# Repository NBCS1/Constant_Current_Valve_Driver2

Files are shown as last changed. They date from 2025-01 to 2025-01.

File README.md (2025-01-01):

# Constant_Current_Valve_Driver
Harware and firmware associated with controlling 4 bistable valves from TTL pulse of various duration. The Pulse is coming from a Pressure controller and its software were only the duration can be set. Different durations trigger different combinations of valves in the context of a microfluidic system.
The valves are bistable and require a pulse of constant current to turn ON/OFF. 
The code can be modified to have any pulse duration and the hardware can be modified to also obtain stable current from 0 to 1.5A.
The stable current is based on a AL8860 ic.
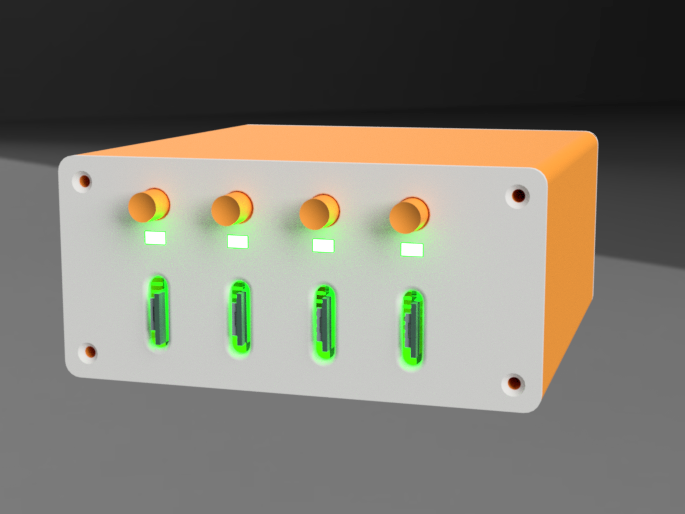
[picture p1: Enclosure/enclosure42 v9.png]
Enclosure


Disclaimer: We will not be responsible in case any implementation of the content of this repository leads to damage in instruments or components.

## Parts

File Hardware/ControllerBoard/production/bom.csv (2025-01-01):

Designator | Footprint | Quantity | Value | LCSC Part #
J1, J2 | PinHeader_1x15_P2.54mm_Vertical | 2 | Conn_01x15_Pin
J10 | PinSocket_1x12_P2.54mm_Vertical | 1 | register_out
J3 | TerminalBlock_Phoenix_PT-1,5-2-5.0-H_1x02_P5.00mm_Horizontal | 1 | power
J4 | PinSocket_1x04_P2.54mm_Vertical | 1 | LEDS_vcc
J5 | PinSocket_1x04_P2.54mm_Vertical | 1 | LEDS_gnd
J6 | PinSocket_1x04_P2.54mm_Vertical | 1 | Buttons_digital
J7 | PinSocket_1x04_P2.54mm_Vertical | 1 | BUTTONS_gnd
J8 | PinSocket_1x04_P2.54mm_Vertical | 1 | oled
J9 | PinSocket_1x02_P2.54mm_Vertical | 1 | TTLin
R1, R2, R3 | 1206 | 3 | 10k
RV1, RV2, RV3, RV4 | Potentiometer_Vishay_T73XW_Horizontal | 4 | potentiometer_3362P
U1, U2 | D16-M | 2 | SN74HC595_N_16
U3 | D14-M | 1 | LM324N
U4 | SOIC20 | 1 | 74HC540D
U5, U6 | SOT108-1_NEX-M | 2 | 74HC08D_652

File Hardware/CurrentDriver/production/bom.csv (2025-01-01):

Designator | Footprint | Quantity | Value | LCSC Part #
C1, C2, C3, C4 | 0805 | 4 | C10µF_0805
C5, C7 | 0805 | 2 | C0.100µF_0805
C6, C8 | 0805 | 2 | C0.0.1µF_0805
D1 | D_SOD-123F | 1 | SS24FL
D2, D4, D6, D7 | 0805 | 4 | LG R971-KN1
J1 | PinHeader_1x04_P2.54mm_Vertical | 1 | Conn_01x04
J10 | PinHeader_1x08_P2.54mm_Vertical | 1 | Conn_01x08
J3 | TerminalBlock_Phoenix_PT-1,5-2-5.0-H_1x02_P5.00mm_Horizontal | 1 | power
J4 | CON_527460871_MOL | 1 | 527460871
L1 | IND_BOURNS_RLB0914 | 1 | RLB0914-37µH
R1 | 1206 | 1 | R125m_1206
R10, R11, R6, R8 | 1206 | 4 | 150ohms
R2, R3 | 1206 | 2 | 7kohms
R4, R5 | 1206 | 2 | 10kohms
U1, U2 | TSOT26-P7_DIO | 2 | AP22615AWU-7
V1 | TSOT25_WT_DIO | 1 | AL8860WT

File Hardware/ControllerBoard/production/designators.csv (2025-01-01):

J1:1
J10:1
J2:1
J3:1
J4:1
J5:1
J6:1
J7:1
J8:1
J9:1
R1:1
R2:1
R3:1
REF**:3
RV1:1
RV2:1
RV3:1
RV4:1
U1:1
U2:1
U3:1
U4:1
U5:1
U6:1

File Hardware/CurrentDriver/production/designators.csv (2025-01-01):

C1:1
C2:1
C3:1
C4:1
C5:1
C6:1
C7:1
C8:1
D1:1
D2:1
D4:1
D6:1
D7:1
J1:1
J10:1
J3:1
J4:1
L1:1
R1:1
R10:1
R11:1
R2:1
R3:1
R4:1
R5:1
R6:1
R8:1
REF**:2
U1:1
U2:1
V1:1

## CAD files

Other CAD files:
Enclosure/button_v15.f3d
Enclosure/enclosure42_v33.f3z

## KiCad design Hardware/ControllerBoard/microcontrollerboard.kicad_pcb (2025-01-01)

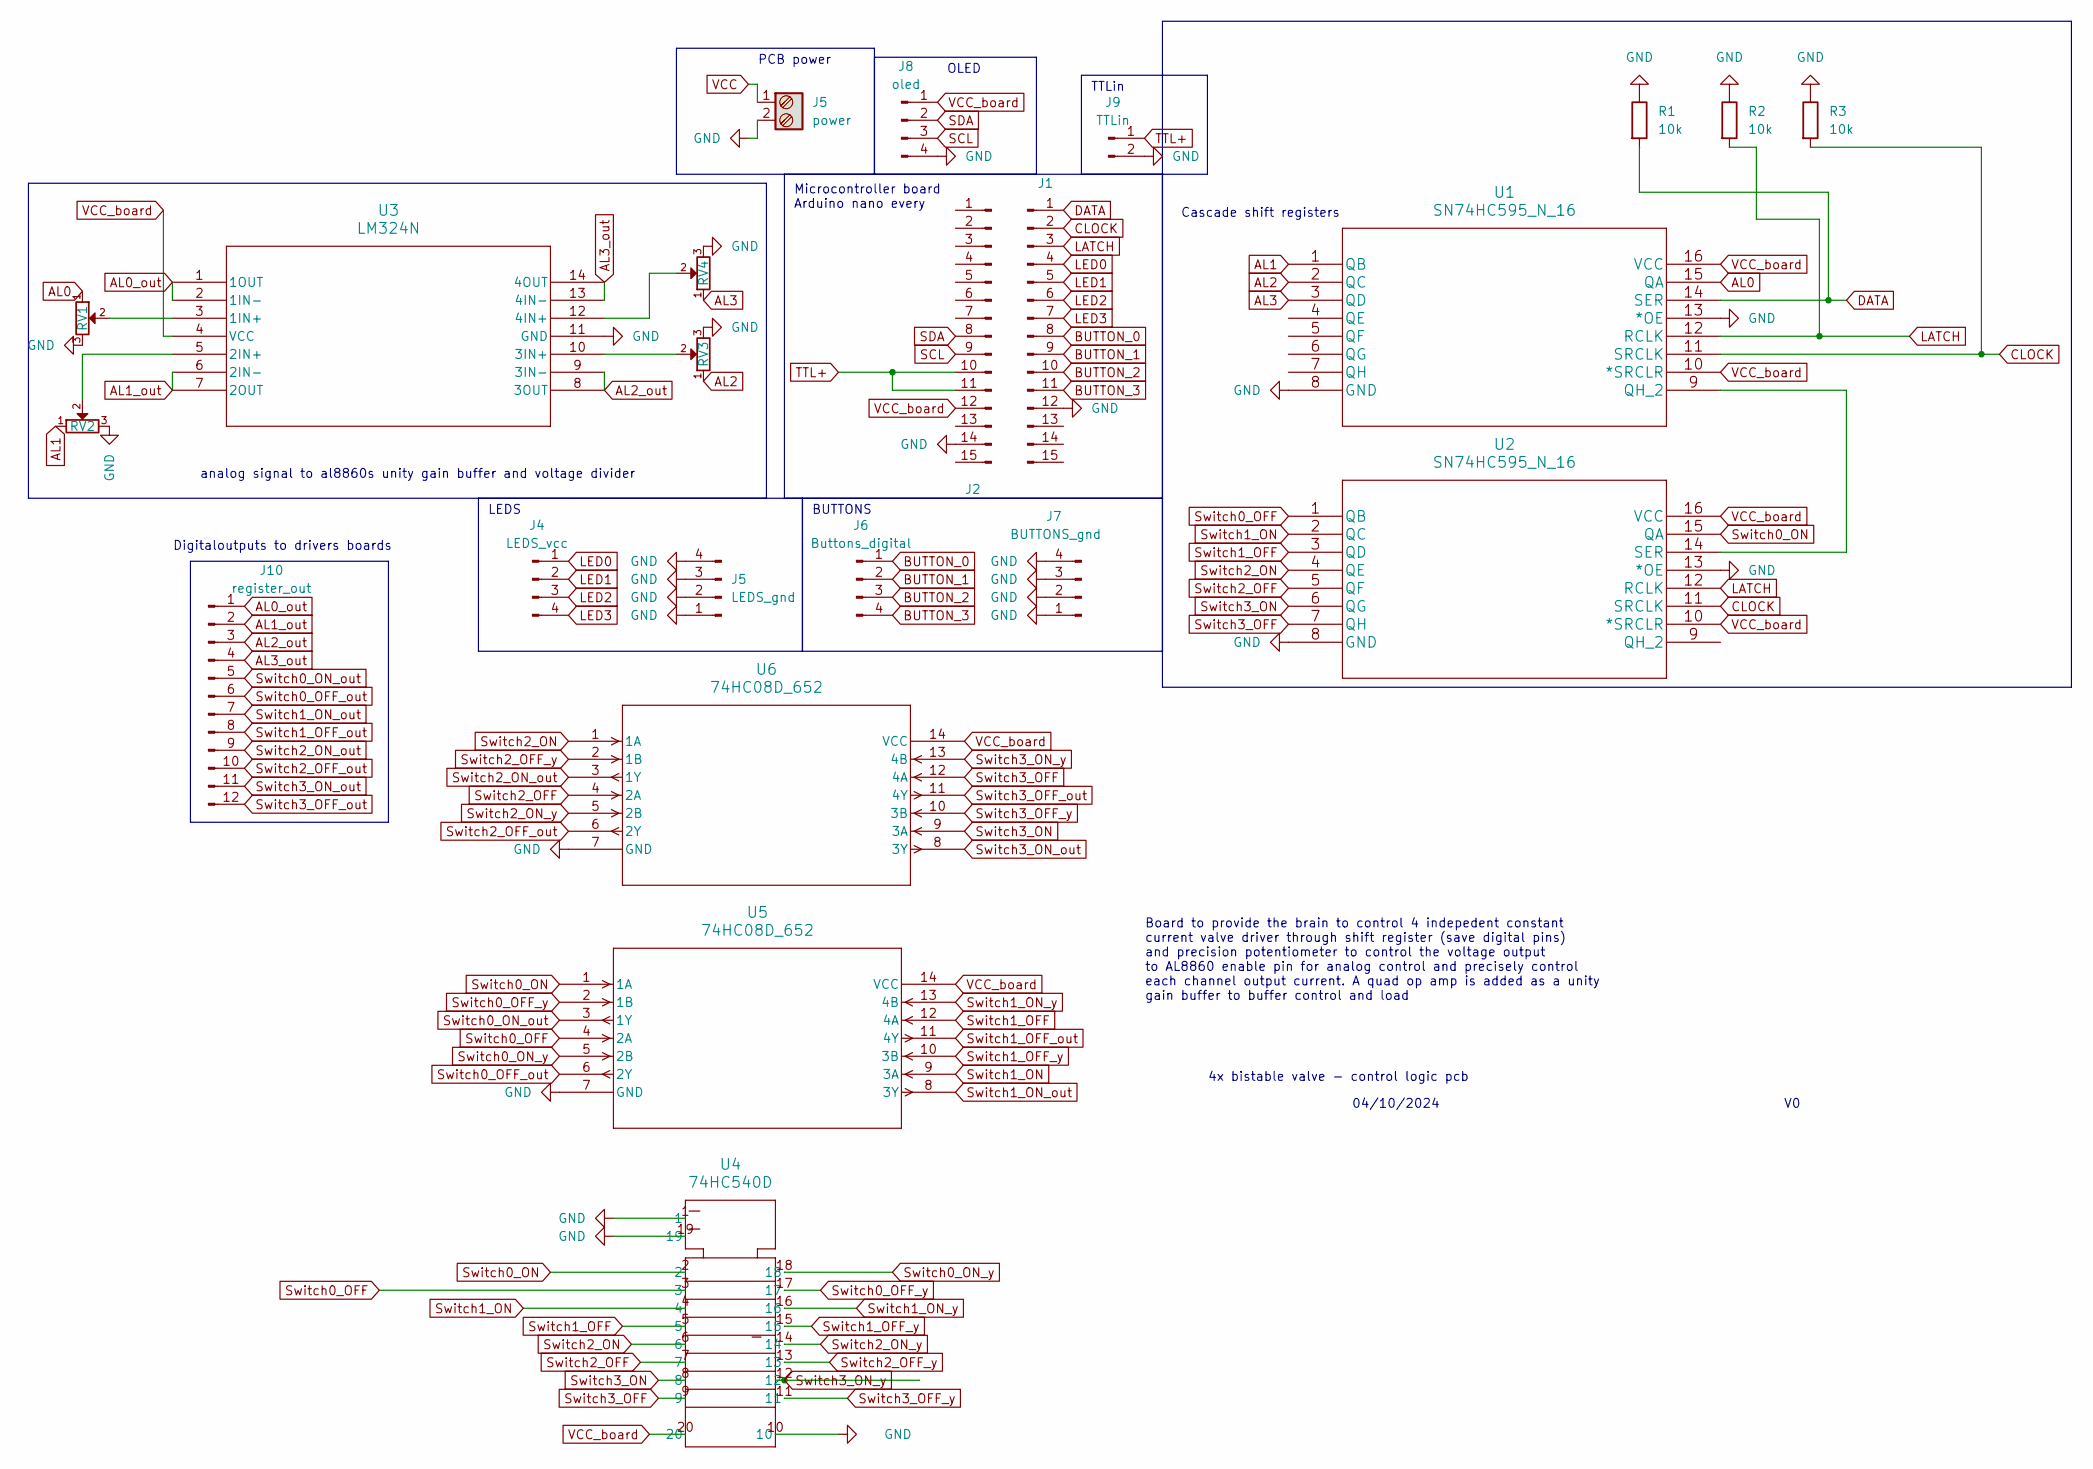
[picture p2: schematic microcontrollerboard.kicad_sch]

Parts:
J1, J2: Conn_01x15_Pin; PinHeader_1x15_P2.54mm_Vertical
J4: LEDS_vcc; PinSocket_1x04_P2.54mm_Vertical
J5: power; TerminalBlock_Phoenix_PT-1,5-2-5.0-H_1x02_P5.00mm_Horizontal
J6: Buttons_digital; PinSocket_1x04_P2.54mm_Vertical
J7: BUTTONS_gnd; PinSocket_1x04_P2.54mm_Vertical
J8: oled; PinSocket_1x04_P2.54mm_Vertical
J9: TTLin; PinSocket_1x02_P2.54mm_Vertical
J10: register_out; PinSocket_1x12_P2.54mm_Vertical
R1, R2, R3: 10k; R_1206_3216Metric_Pad1.30x1.75mm_HandSolder
RV1, RV2, RV3, RV4: potentiometer_3362P; Potentiometer_Vishay_T73XW_Horizontal
U1, U2: SN74HC595_N_16; D16-M
U3: LM324N; D14-M
U4: 74HC540D; SOIC20
U5, U6: 74HC08D_652; SOT108-1_NEX-M

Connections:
AL0: RV1.1, U1.15 (QA)
AL0_out: J10.1, U3.1 (1OUT), U3.2 (1IN-)
AL1: RV2.1, U1.1 (QB)
AL1_out: J10.2, U3.6 (2IN-), U3.7 (2OUT)
AL2: RV3.1, U1.2 (QC)
AL2_out: J10.3, U3.8 (3OUT), U3.9 (3IN-)
AL3: RV4.1, U1.3 (QD)
AL3_out: J10.4, U3.13 (4IN-), U3.14 (4OUT)
BUTTON_0: J1.8, J6.1
BUTTON_1: J1.9, J6.2
BUTTON_2: J1.10, J6.3
BUTTON_3: J1.11, J6.4
CLOCK: J1.2, R3.2, U1.11 (SRCLK), U2.11 (SRCLK)
DATA: J1.1, R1.2, U1.14 (SER)
LATCH: J1.3, R2.2, U1.12 (RCLK), U2.12 (RCLK)
LED0: J1.4, J4.1
LED1: J1.5, J4.2
LED2: J1.6, J4.3
LED3: J1.7, J4.4
unnamed: U1.9 (QH_2), U2.14 (SER)
unnamed: RV1.2, U3.3 (1IN+)
unnamed: RV2.2, U3.5 (2IN+)
unnamed: RV3.2, U3.10 (3IN+)
unnamed: RV4.2, U3.12 (4IN+)
SCL: J2.9, J8.3
SDA: J2.8, J8.2
Switch0_OFF: U2.1 (QB), U4.3, U5.4 (2A)
Switch0_OFF_out: J10.6, U5.6 (2Y)
Switch0_OFF_y: U4.17, U5.2 (1B)
Switch0_ON: U2.15 (QA), U4.2, U5.1 (1A)
Switch0_ON_out: J10.5, U5.3 (1Y)
Switch0_ON_y: U4.18, U5.5 (2B)
Switch1_OFF: U2.3 (QD), U4.5, U5.12 (4A)
Switch1_OFF_out: J10.8, U5.11 (4Y)
Switch1_OFF_y: U4.15, U5.10 (3B)
Switch1_ON: U2.2 (QC), U4.4, U5.9 (3A)
Switch1_ON_out: J10.7, U5.8 (3Y)
Switch1_ON_y: U4.16, U5.13 (4B)
Switch2_OFF: U2.5 (QF), U4.7, U6.4 (2A)
Switch2_OFF_out: J10.10, U6.6 (2Y)
Switch2_OFF_y: U4.13, U6.2 (1B)
Switch2_ON: U2.4 (QE), U4.6, U6.1 (1A)
Switch2_ON_out: J10.9, U6.3 (1Y)
Switch2_ON_y: U4.14, U6.5 (2B)
Switch3_OFF: U2.7 (QH), U4.9, U6.12 (4A)
Switch3_OFF_out: J10.12, U6.11 (4Y)
Switch3_OFF_y: U4.11, U6.10 (3B)
Switch3_ON: U2.6 (QG), U4.8, U6.9 (3A)
Switch3_ON_out: J10.11, U6.8 (3Y)
Switch3_ON_y: U4.12, U6.13 (4B)
TTL+: J2.10, J2.11, J9.1
VCC_board: J2.12, J8.1, U1.10 (*SRCLR), U1.16 (VCC), U2.10 (*SRCLR), U2.16 (VCC), U3.4 (VCC), U4.20, U5.14 (VCC), U6.14 (VCC)

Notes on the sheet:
Digitaloutputs to drivers boards
Cascade shift registers
04/10/2024
Board to provide the brain to control 4 indepedent constant current valve driver through shift register (save digital pins) and precision potentiometer to control the voltage output to AL8860 enable pin for analog control and precisely control each channel output current. A quad op amp is added as 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
PCB power
BUTTONS
OLED
Microcontroller board Arduino nano every
analog signal to al8860s unity gain buffer and voltage divider
LEDS
TTLin
4x bistable valve - control logic pcb

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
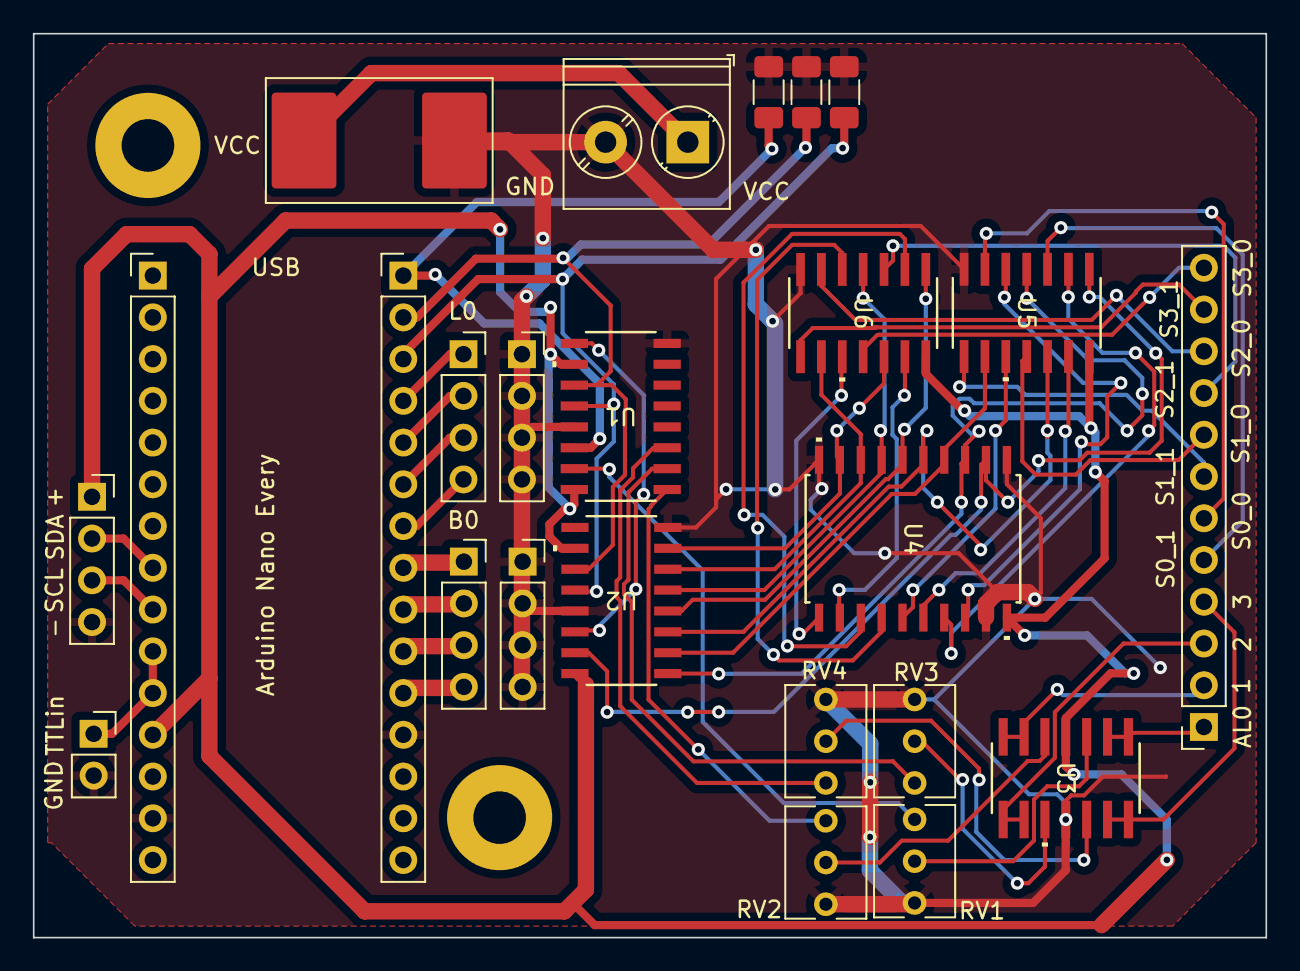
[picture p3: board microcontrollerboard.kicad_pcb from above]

Board: 2 copper layers, 75.0 x 55.0 mm, 23 parts (0 on the bottom side), 53 nets.

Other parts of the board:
J3: power; TerminalBlock_Phoenix_PT-1,5-2-5.0-H_1x02_P5.00mm_Horizontal

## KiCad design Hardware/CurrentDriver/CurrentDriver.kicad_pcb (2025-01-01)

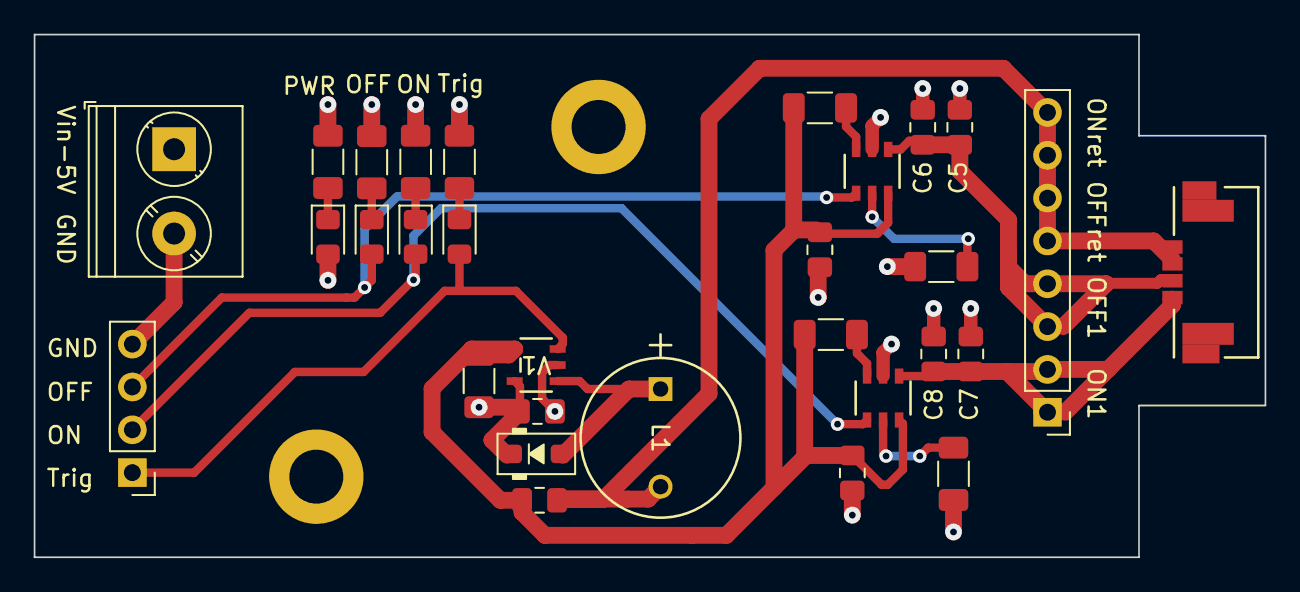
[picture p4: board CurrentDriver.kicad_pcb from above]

Board: 4 copper layers, 73.0 x 31.0 mm, 30 parts (0 on the bottom side), 18 nets.

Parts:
C1, C2, C3, C4: C10µF_0805; C_0805_2012Metric_Pad1.18x1.45mm_HandSolder
C5, C7: C0.100µF_0805; C_0805_2012Metric_Pad1.18x1.45mm_HandSolder
C6, C8: C0.0.1µF_0805; C_0805_2012Metric_Pad1.18x1.45mm_HandSolder
D1: SS24FL; D_SOD-123F
D2, D4, D6, D7: LG R971-KN1; LED_0805_2012Metric_Pad1.15x1.40mm_HandSolder
J1: Conn_01x04; PinHeader_1x04_P2.54mm_Vertical
J3: power; TerminalBlock_Phoenix_PT-1,5-2-5.0-H_1x02_P5.00mm_Horizontal
J4: 527460871; CON_527460871_MOL
J10: Conn_01x08; PinHeader_1x08_P2.54mm_Vertical
L1: RLB0914-37µH; IND_BOURNS_RLB0914
R1: R125m_1206; R_1206_3216Metric_Pad1.30x1.75mm_HandSolder
R2, R3: 7kohms; R_1206_3216Metric_Pad1.30x1.75mm_HandSolder
R4, R5: 10kohms; R_1206_3216Metric_Pad1.30x1.75mm_HandSolder
R6, R8, R10, R11: 150ohms; R_1206_3216Metric_Pad1.30x1.75mm_HandSolder
U1, U2: AP22615AWU-7; TSOT26-P7_DIO
V1: AL8860WT; TSOT25_WT_DIO

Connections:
AP_+_1: C1.2, C3.2, C4.2, R1.1, R4.2, R5.2, U1.6 (in), U2.6 (in), V1.4 (SET)
AP_-_1: C1.1, J4.5, J4.6, J4.7, J4.8, J10.5, J10.6, J10.7, J10.8, L1.2
GND: C2.2, C3.1, C4.1, C5.1, C6.1, C7.1, C8.1, J1.4, J3.2, R2.2, R3.2, R6.2, R8.2, R10.2, R11.2, U1.2 (gnd), U2.2 (gnd), V1.2 (GND)
unnamed: D1.2 (A), L1.1, V1.1 (SW)
unnamed: D2.1 (K), R6.1
unnamed: D4.1 (K), R8.1
unnamed: D6.1 (K), R10.1
unnamed: D7.1 (K), R11.1
unnamed: R5.1, U1.3 (flg)
unnamed: R2.1, U1.5 (iset)
unnamed: R4.1, U2.3 (flg)
unnamed: R3.1, U2.5 (iset)
VCC: C2.1, D1.1 (K), D4.2 (A), J3.1, R1.2, V1.5 (VIN)
VtrigAL_1: D2.2 (A), J1.1, V1.3 (CTRL)
VtrigOFF_1: D7.2 (A), J1.3, U2.4 (en)
VtrigON_1: D6.2 (A), J1.2, U1.4 (en)
load_off_1: C5.2, C6.2, J4.3, J4.4, J10.3, J10.4, U2.1 (out)
load_on_1: C7.2, C8.2, J4.1, J4.2, J10.1, J10.2, U1.1 (out)

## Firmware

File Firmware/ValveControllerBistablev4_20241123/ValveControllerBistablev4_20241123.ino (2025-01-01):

// Import libraries
#include <Wire.h>
#include <Adafruit_GFX.h>
#include <Adafruit_SSD1306.h>

// Define pins
#define SDA_PIN 19
#define SCL_PIN 18
#define NUM_LEDS 4
#define NUM_BUTTONS 4
int dataPin = 12;      // Set the data pin
int latchPin = 10;
int clockPin = 11;
int ttlPin1 = 20;       // Set TTL pin 1
int ttlPin2 = 21;       // Set TTL pin 2 
int buttonPins[NUM_BUTTONS] = {5, 4, 3, 2}; // Button pins
int ledPins[NUM_LEDS] = {9, 8, 7, 6};      // LED pins
int stateValve[NUM_LEDS] = {0, 0, 0, 0};    // Valve states
int stateButton[NUM_BUTTONS] = {0, 0, 0, 0}; // Button states

// Declare OLED
Adafruit_SSD1306 display(128, 32, &Wire, -1);

// Debounce time
static uint32_t lastDebounceTime = 0;
static uint32_t debounceDelay = 50;

// Variables
int triggerPulseDuration = 500;
unsigned int binaryReset = 0b0000000000000000;
unsigned int dataSend = 0b0000000001010101;
int toggledValve = -1;

//Pulse detection variables
volatile unsigned long pulseStart = 0; // Variable to store the pulse start time
volatile unsigned long pulseEnd = 0; // Variable to store the pulse end time
volatile boolean pulse1=false;
volatile boolean pulse2=false;
unsigned long Start=0;
unsigned long End=0;
unsigned long duration=0;

// Function to update OLED valve status during button overrides
String statePrint(const int index) {
  String output = "v" + String(index + 1) + ":";
  output += stateValve[index] == 1 ? "ON" : "OFF";
  if (index % 2 == 0)
    output += "/";
  return output;
}

// Function to shift out 16 bits
void shiftOut16(int dataPin, int clockPin, unsigned int value) {
  shiftOut(dataPin, clockPin, LSBFIRST, value);  // Send upper 8 bits
  shiftOut(dataPin, clockPin, LSBFIRST, (value >> 8)); // Send lower 8 bits
}

// Function to update shift register
void updateShiftRegister(unsigned int value) {
  digitalWrite(latchPin, LOW);               // Prepare for data transmission
  shiftOut16(dataPin, clockPin, value); 
  // Shift out the 16 bits
  digitalWrite(latchPin, HIGH);              // Latch the data to output it
}

// Function to clear the shift register (set all outputs to LOW)
void clearShiftRegister() {
  updateShiftRegister(binaryReset);  // Shift out all 0s
}

// Update valve states based on the received value
void updateStates(int value) {
  byte valveBits = value & 0xFF;  // Mask to get the last 8 bits

  for (int i = 0; i < NUM_LEDS; i++) {
    // Reverse the order of reading the bits
    byte bitPair = (valveBits >> ((NUM_LEDS - 1 - i) * 2)) & 0b11;

    if (bitPair == 0b01) {
      stateValve[i] = 0;  // Valve is off
    } else if (bitPair == 0b10) {
      stateValve[i] = 1;  // Valve is on
    } else {
      stateValve[i] = -1; // Undefined or invalid state
    }
  }

  // Update stateButton array
  for (int i = 0; i < NUM_BUTTONS; i++) {
    stateButton[i] = stateValve[i];
  }
    for (int i=0; i<NUM_LEDS;i++){
    digitalWrite(ledPins[i], stateValve[i]);
  }
}



// Update valves based on button state
void valveUpdate(int value) {
  uint16_t truncatedValue = value & 0b0000111111111111;// Keep the switches sequence but don't turn the current ON yet otherwise current rush overflow
  updateShiftRegister(truncatedValue);
  delay(1000); //let's the switches open
  updateShiftRegister(value);      // Triggers the right valves combination through switches
  delay(triggerPulseDuration);     // With a x ms pulse 500
  updateStates(value);
  clearShiftRegister(); 
}

unsigned int createBinaryNumber(int toggledValve) {
    unsigned int binaryNumber = 0b11110000;  // Start with the first 8 bits

    // Loop through each LED to set the correct bits
    for (int i = 0; i < NUM_LEDS; i++) {
        unsigned int valveBits = 0b00; // Default to 00

        // Determine the bits to append based on the valve's state

        if (toggledValve == i){
          if (stateValve[i] == 1) {  // Valve is ON
            valveBits = 0b01;  // Set bits to 10 for OFF
        } else if (stateValve[i] == 0) {  // Valve is OFF
            valveBits = 0b10;  // Set bits to 01 for ON
        }}else if (toggledValve != i){
                    if (stateValve[i] == 1) {  // Valve is ON
              valveBits = 0b10;  // Set bits to 10 for ON
          } else if (stateValve[i] == 0) {  // Valve is OFF
              valveBits = 0b01;  // Set bits to 01 for OFF
          }
        }

        // Replace the corresponding pair of bits for the toggled valve
        binaryNumber = (binaryNumber << 2) | valveBits;
    }

    return binaryNumber;
}

void displayConfig(String a,String b,String c){
  display.clearDisplay();
  display.setTextSize(1.5);
  display.setTextColor(SSD1306_WHITE);
  display.setCursor(0,0);
  display.println(a);
  display.println(b);
  display.println(c);
  display.setCursor(0,0);
  display.display();
}
void pulseStartISR() { pulse1 = true; }// Rising flag
void pulseEndISR() { pulse2 = true; }// Falling flag

// Setup function
void setup() {
  pinMode(dataPin, OUTPUT);
  pinMode(clockPin, OUTPUT);
  pinMode(latchPin, OUTPUT);
  digitalWrite(dataPin, LOW);
  digitalWrite(clockPin, LOW);
  digitalWrite(latchPin, LOW);
  clearShiftRegister();
  dataSend = 0b1111000001010101;
  valveUpdate(dataSend);
  // Attach interrupts to the input pin, pulseStartISR for RISING and pulseEndISR for FALLING
  attachInterrupt(digitalPinToInterrupt(ttlPin1), pulseStartISR, RISING);
  attachInterrupt(digitalPinToInterrupt(ttlPin2), pulseEndISR, FALLING);
  // Open I2C communication with OLED display
  Wire.begin();


  // Set button and LED modes
  for (int i = 0; i < NUM_BUTTONS; i++) {
    pinMode(buttonPins[i], INPUT_PULLUP);
  }
  for (int i = 0; i < NUM_LEDS; i++) {
    pinMode(ledPins[i], OUTPUT);
    digitalWrite(ledPins[i], LOW); // Turn off LEDs
  }


  // Set everything to OFF hardware and software-wise
  clearShiftRegister();
  stateValve[0] = 0; // Initialize valve states
  stateValve[1] = 0;
  stateValve[2] = 0;
  stateValve[3] = 0;
  stateButton[0] = 0; // Initialize button states
  stateButton[1] = 0;
  stateButton[2] = 0;
  stateButton[3] = 0;

  // Initiate display
  display.begin(SSD1306_SWITCHCAPVCC, 0x3C); // Address 0x3C for 128x32
  display.clearDisplay();
  displayConfig("Hello", "Microfluidic", "User");
  display.display();
}

// Main loop
void loop() {
  // Serial input logic
  if (pulse1){
    pulse1=false;
    Start=micros();
    //Serial.println("yes detected");
  }
  if (pulse2){
    End=micros();
    pulse2=false;
    duration=(End-Start)/1000;
    if (duration > 0) {
      if (duration < 15) { // Reset
        dataSend = 0b1111000001010101;
        valveUpdate(dataSend);
        displayConfig("Config. all off", "Tube 1 -> OFF", "Tube 2 -> OFF");
      } else if (duration < 80) { // Treatment
        dataSend = 0b1111000001101001;
        valveUpdate(dataSend);
        displayConfig("Config. treatment", "Tube 1 -> Trash", "Tube 2 -> Chip");
      } else if (duration < 150) { // All trash
        dataSend = 0b1111000001100110;
        valveUpdate(dataSend);
        displayConfig("Config. all trash", "Tube 1 -> Trash", "Tube 2 -> Trash");
      } else if (duration < 250) { // All chip
        dataSend = 0b111100010011001;
        valveUpdate(dataSend);
        displayConfig("Config. all chip", "Tube 1 -> Chip", "Tube 2 -> Chip");
      } else if (duration < 350) { // Control
        dataSend = 0b1111000010010110;
        valveUpdate(dataSend);
        displayConfig("Config. control", "Tube 1 -> Chip", "Tube 2 -> Trash");
      } else {
        dataSend = 0b1111000001010101;
        valveUpdate(dataSend);
        displayConfig("Trigger duration", "detected", "is wrong");
      }

      display.display();
    }
  }

  // Button logic remains unchanged
  for (int i = 0; i < NUM_BUTTONS; i++) {
    int reading = digitalRead(buttonPins[i]);

    if (reading != stateButton[i]) {
      if (millis() - lastDebounceTime > debounceDelay) {
        stateButton[i] = reading;

        if (stateButton[i] == LOW) {  // Button pressed
          toggledValve = i;  // Track which valve to toggle
          unsigned int binaryNumber = createBinaryNumber(toggledValve);
          valveUpdate(binaryNumber);
          clearShiftRegister();            // Clear the shift register, valves are bistable
                            // Display valve states
        display.clearDisplay();
        display.setCursor(0, 0);
        display.println(statePrint(0) + statePrint(1));
        display.println(statePrint(2) + statePrint(3));
        display.println("Manual override");
        display.display();
        }
        lastDebounceTime = millis();
      }

    }

      
  }
   //Control leds according to stateValve

}
